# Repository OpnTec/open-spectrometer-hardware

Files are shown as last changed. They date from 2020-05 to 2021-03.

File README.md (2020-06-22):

# DIY Analytics Open Source Spectrometer




This repository provides hardware schematics and list of materials for the open spectrometer project to enable practitioners, students and citizen scientists to collect data with their spectrometer and have a good and fun learning experience. The open spectrometer project consists of a web cam, simple lasercut parts, battery casing and a suitable LED lightning component. The spectrometer connects to a computer via USB, where the user can run the scripts provided in this repository to run experiments and take measurements. Enjoy!

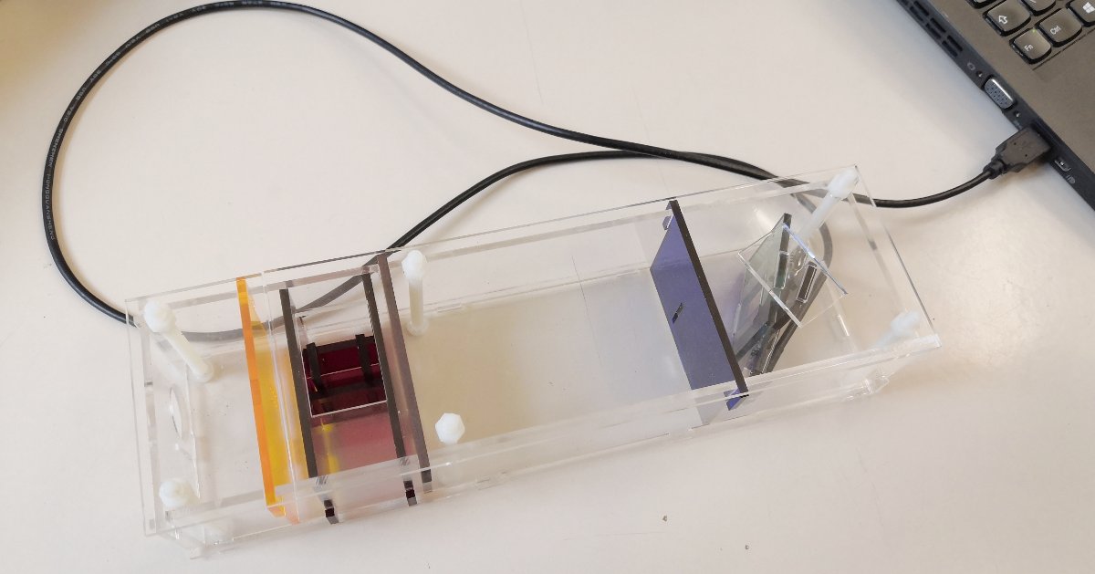
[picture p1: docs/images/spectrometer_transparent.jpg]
Open Source Spectrometer Open Source Spetrometer

A transparent version of the spectrometer for explanation purposes.

## Open Science and Goals

By definition science should be open and reproducible. So, the outcome of an experiment can be verified by anyone. Unfortunately today this is not always the case. In order to be able to verify experiments all components used should be openly accessible. This includes the software and hardware of scientific instruments. Our spectrometer project follows this path. By giving access to all layers of the device used in a scientific experiment users can develop a deep understanding how scientific measurements are taken and practitioners are able to critically understand the limitations of the particular instrument.

The spectrometer consists of a set of materials designed to be available and affordable anywhere in the world. The design's focus is to promote education about spectrometry and analytical chemistry, with the goal of empowering, stimulating and encouraging individuals to learn about their environment applying scientific methodologies. Furthermore, the goal of the tool is to enable practitioners to study open design, scientific programming, physics and to reflect about reproducibility in scientific practices.

## Communication

The spectrometer community is still small. There are overlaps with the Pocket Science Lab team. To stay connected with different community members we continue to use the PSLab Gitter channel for the beginning. We will set up a dedicated channel once the project is more established. Please join us here:
* [Pocket Science Channel](https://gitter.im/fossasia/pslab)

## Features and Implementation Status

- The bill of materials is available in the /components folder.
- The design files for the lasercut files are available in the /schematics folder.

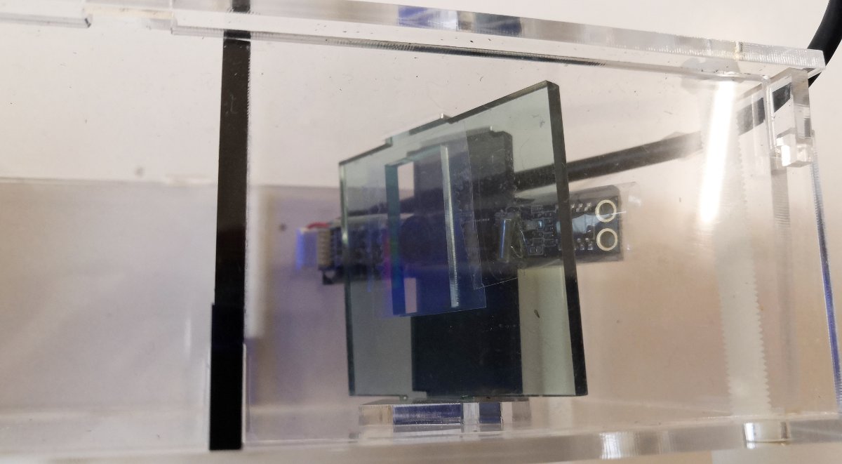
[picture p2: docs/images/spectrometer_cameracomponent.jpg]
Open Source Spectrometer Camera Component Open Source Spetrometer Camera Component

The camera component of the spectrometer in transparent casing.

Roadmap:

- improve the design of the wooden part holding the camera
- redesign the light side, in order to allow CFL light coming in without disassembling the whole spectrometer
- write a script that allows the user to control the spactrometer with a simple offline device
- reduce the size to fit in one 25x50cm board

## Software

To get the data from the spetrometer device practitioners can use the spectrometer Python scripts available in the project. 

## Contributors

Alessandro Volpato is the creator of the project. The work was done by merging concepts of the [Public Lab Spectrometer](https://publiclab.org/notes/abdul/10-13-2016/desktop-spectrometry-starter-kit-3-0-instructions), 
the [GaudiLabs spectrometer](http://www.gaudi.ch/GaudiLabs/?page_id=328) and creating new design features to simplify the assembly of a lasercut spetrometer.

## License

The repository is licenced under CERN Open Hardware Licence v1.2

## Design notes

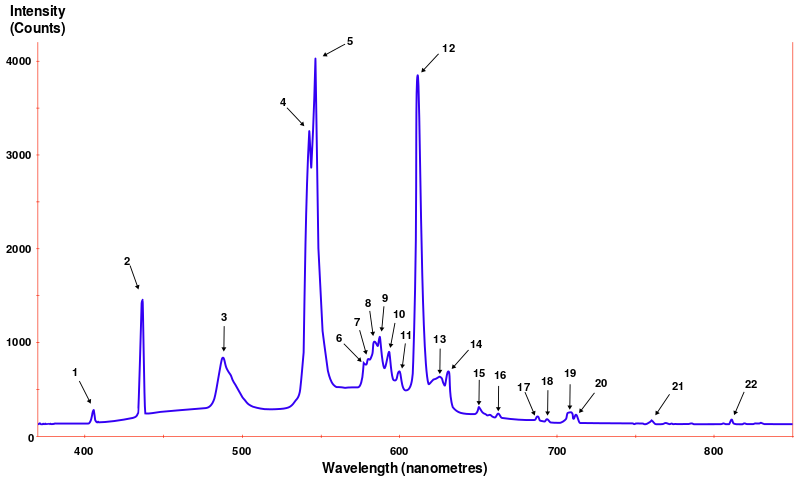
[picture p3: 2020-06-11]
open-spectrometer_v1/docs/images/Fluorescent_lighting_spectrum_peaks_labelled.svg.png

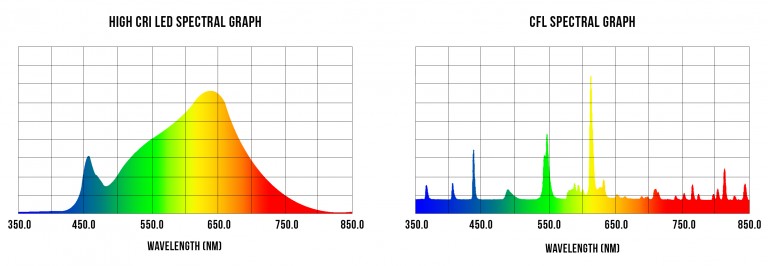
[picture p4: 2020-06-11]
open-spectrometer_v1/docs/images/High-CRI-vs-CFL-Spectrum-Graph-768x266.jpg

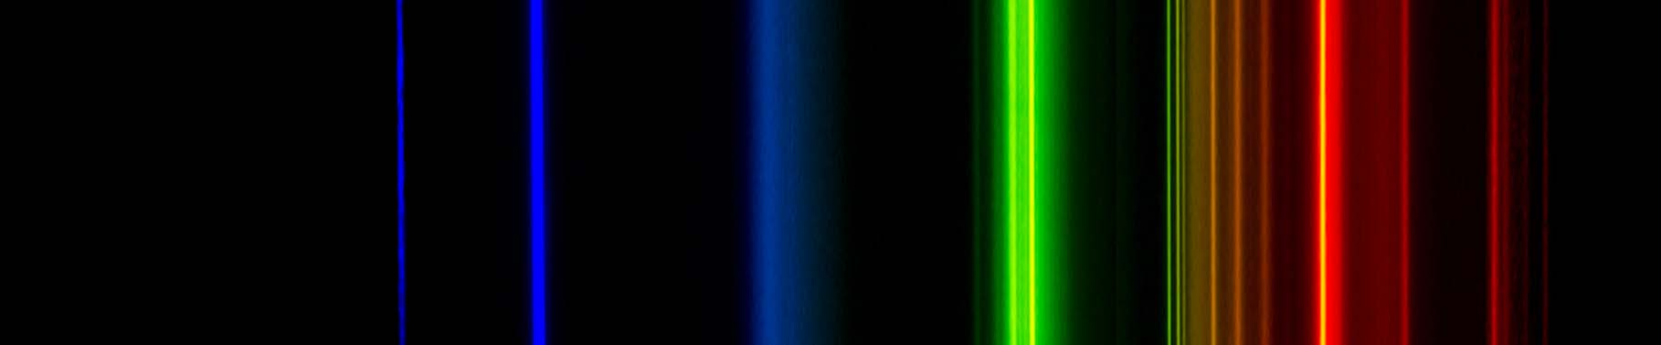
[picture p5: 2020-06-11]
open-spectrometer_v1/docs/images/3rdPolySnowy1818.jpg

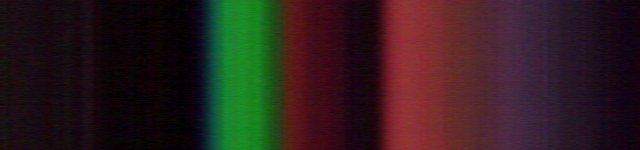
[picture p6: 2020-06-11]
open-spectrometer_v1/docs/images/2018_9_3_basil.png

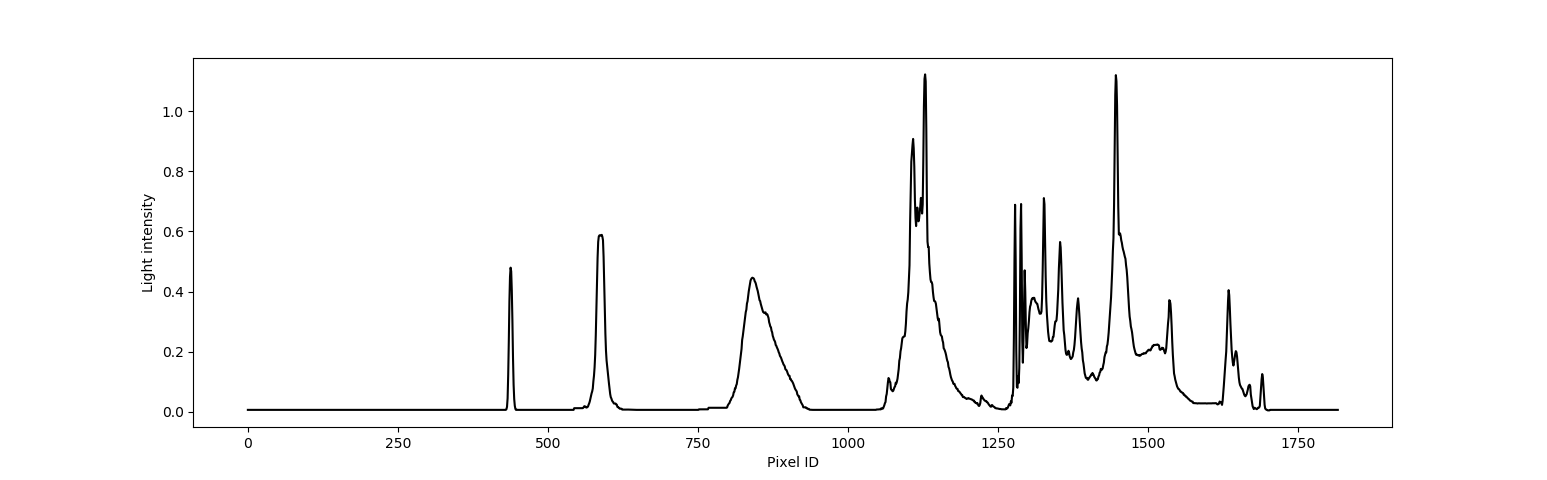
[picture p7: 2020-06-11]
open-spectrometer_v1/docs/images/cfl_BW.png

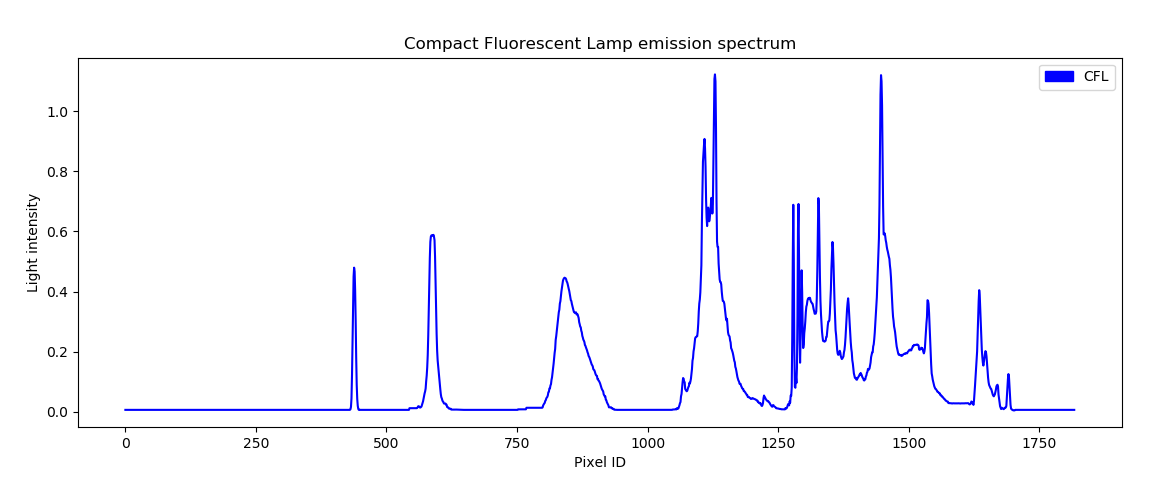
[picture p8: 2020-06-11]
open-spectrometer_v1/docs/images/CFL_rawPlot.png

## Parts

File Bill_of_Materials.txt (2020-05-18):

Bill of materials

- 2x MDF wood plates 25x50 cm (to be lasercut)
- Screws and nuts M5 60 mm
- Screws M15 and nuts M15 width max 3mm
- Anti slip tiny silicon pads
- Razor blades
- Duct tape / light tight tape
- Diffraction grating or "peeled" CD
- Webcam VIDEW JDEPC-05, lens 45°

- 1,5V batteries holder, double slot
- 2x 1,5V batteries
- White LED
- CFL (Compact Fluorescent Light) - for calibration (Notmandatory)
- Plug for the lightbulb

Suppliers:
MDF: Modulor, Berlin, Germany
https://www.modulor.de/en/

Screws and nuts M5x60
Aliexpress
Screws???
https://www.aliexpress.com/item/4000138361051.html

Screws and nuts M1.4x6
Aliexpress
https://www.aliexpress.com/item/32998910287.html
https://www.aliexpress.com/item/33002547187.html

Anti-slip pads
https://www.aliexpress.com/item/4000139088828.html

Slit / razor blades
https://www.edmundoptics.com/f/precision-air-slits/12136/
https://www.dm.de/muehle-rasierklingen-fuer-rasierhobel-p4028982008452.html

Duct tape
At bricolage market. It is used to cover the green LED on the camera module
To check if it's easier to turn off the LED directly

Diffraction grating / peeled cd
https://www.amazon.de/Rolle-Beugungsgitter-Folien-Linear-Linien/dp/B007G0MW2Q

Webcam VIDEW JDEPC-05, lens 45°, without IR filter
https://www.alibaba.com/product-detail/1-4-CMOS-Sensor-720P-camera_60667541444.html

AA battery x2
https://www.aliexpress.com/item/4000194009848.html

AA battery double case
https://www.aliexpress.com/item/32818907820.html

White LED
https://www.aliexpress.com/item/32505130071.html

CFL lightbulb (It's being phased out, xenon discharge lamps can substitute them)
https://www.amazon.de/Osram-Energiesparlampe-Stick-E27-363855/dp/B008OJWF9S/

CFL E27 lamp holder
https://www.amazon.de/kwmobile-Lampenfassung-Schalter-Lampenaufh%C3%A4ngung-Pendelleuchte/dp/B0769XRYXL

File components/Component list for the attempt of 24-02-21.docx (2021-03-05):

OLD Parts for assembling the driver circuit board

Suppliers:

Capacitors:

1x 0,1 µF

https://www.mouser.de/Passive-Components/Capacitors/Ceramic-Capacitors/MLCCs-Multilayer-Ceramic-Capacitors/Multilayer-Ceramic-Capacitors-MLCC-SMD-SMT/_/N-bkrdv?P=1z0wqusZ1yx4aw4Z1yzmou0&Keyword=capacitor&FS=True

1x 10 µF (tantalum) 10 µF (MLCC or tantalum 1206)
https://www.mouser.de/Passive-Components/Capacitors/Tantalum-Capacitors/Tantalum-Capacitors-Solid-SMD/_/N-75hr4?P=1z0wrkrZ1yzmotyZ1yzt832Z1yx4aw4

Resistors:

1x 2,2 kOhm (Better Reichelt)

https://www.conrad.de/de/o/smd-widerstaende-0241260.html?tfo_ATT_LOV_RESISTOR_DESIGN=0805&tfo_ATT_RESISTANCE_VALUE_NUM=2200%20%CE%A9

2x 150 Ohm (Better Reichelt)

https://www.conrad.de/de/o/smd-widerstaende-0241260.html?tfo_ATT_RESISTANCE_VALUE_NUM=150%20%CE%A9&tfo_ATT_LOV_RESISTOR_DESIGN=0805

1x 27 kOm (Better Reichelt)

https://www.mouser.de/Passive-Components/Resistors/_/N-5g9n?P=1yzmou0Z1yzekj3

1x 12 kOhm (Better Reichelt)

https://www.mouser.de/Passive-Components/Resistors/_/N-5g9n?P=1yzmou0Z1yzeki4

Transistor:

1x PNP

https://www.conrad.de/de/f/sot23-1724883.html?tfo_ATT_LOV_MODEL_TRANSISTORS=PNP

Hex-Inverter:

1x (Better Reichelt SMD HC 04 Inverter, Hex)

https://www.conrad.de/de/search.html?search=74HC04D&category=%1Ft12%1Fc1202469

Voltage regulator:

Reference:

https://tcd1304.wordpress.com/driving-circuit-and-pcb/

### Parts and components -> download all datasheets -> check 0603 dimensions

##### Drive circuit:

- C₃, C₄ 100 nF (MLCC 0805)
- C₂ 10 µF (MLCC or tantalum 1206) -> check dimension
- R₄, R₄ 150 Ω (0805)
- R₃ 2.2 kΩ (0805)
- U₂ 74HC04D (SOIC-14) Note: Hex inverter -> check direction
- T₁ 2SA1015 / 2SA1162 (SOT-23) Note: Transistor

##### LDO: low noise low drop-out voltage regulator

- U₁ LT1761-BYP (SOT-23-5) Note: High efficiency, step down, DC-DC converter Low Noise, Low Dropout Micropower Regulator
- R₂ 27 kΩ (0805)
- R₁ 12 kΩ (0805)
- C₁ 10 nF (MLCC 0805) -> check dimension
- C₅ 1 µF (MLCC 0805) -> check dimension

The LDO is an additional circuit to produce, low noise and smoother(?) power supply

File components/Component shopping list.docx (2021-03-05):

Current Version

Parts for assembling the driver circuit board

Supplier: Mouser

Make 1 shipment to check that the dimensions of the SMD parts match with the board!!!

Capacitors:

C1: https://www.mouser.de/ProductDetail/KEMET/C0805C103K8RACTU/?qs=cw4evkOYbeKGik5IKerAPQ%3D%3D

C2: https://www.mouser.de/ProductDetail/ROHM-Semiconductor/TCA0J106M8R/?qs=sGAEpiMZZMsh%252B1woXyUXj69kqxOlrVKzuvW12Vm0Wbs%3D

C3,C4: https://www.mouser.de/ProductDetail/KEMET/C0805C104K9RACAUTO/?qs=ds50AKTGxA84SWre%252BvImOA%3D%3D

C5: https://www.mouser.de/ProductDetail/KEMET/C0805C105K9RACTU/?qs=Nnkldhwoc36daYb4WU%2Fecw%3D%3D

Resistors:

R1: https://www.mouser.de/ProductDetail/Panasonic/ERJ-U06J123V/?qs=sGAEpiMZZMtlubZbdhIBIAOOKAsNLlB%252BU0Q0TtVw5QE%3D

R2: https://www.mouser.de/ProductDetail/Panasonic/ERJ-T06J273V/?qs=sGAEpiMZZMtlubZbdhIBIK7FbVYKWV6W038uxDWOpRk%3D

R3: https://www.mouser.de/ProductDetail/Panasonic/ERJ-U06J222V/?qs=Yyy8avaXlIt9u%2Fm70g0idQ%3D%3D

R4,R5: https://www.mouser.de/ProductDetail/Panasonic/ERJ-U06J151V/?qs=Yyy8avaXlIvde5Eu83MNpg%3D%3D

Transistor:

T1: https://www.mouser.de/ProductDetail/Toshiba/2SA1162-GRLF/?qs=iCzJi%2FIZBF4pKAB14b5rPg%3D%3D

Units:

U1: https://www.mouser.de/ProductDetail/Analog-Devices/LT1761ES5-BYPTRPBF/?qs=ytflclh7QUVO1tv%2FV6bsow%3D%3D

U2: https://www.mouser.de/ProductDetail/Nexperia/74HC04D-Q100118/?qs=%2Fha2pyFadugYAPSa%2Fr415QHV4LwjhLocoaB0htU8Y3E%3D

Reference:

https://tcd1304.wordpress.com/driving-circuit-and-pcb/

### Parts and components -> download all datasheets -> check 0603 dimensions

##### Drive circuit:

- C₃, C₄ 100 nF (MLCC 0805)
- C₂ 10 µF (MLCC or tantalum 1206) -> check dimension
- R₄, R5 150 Ω (0805)
- R₃ 2.2 kΩ (0805)
- U₂ 74HC04D (SOIC-14) Note: Hex inverter -> check direction
- T₁ 2SA1015 / 2SA1162 (SOT-23) Note: Transistor

##### LDO: low noise low drop-out voltage regulator

- U₁ LT1761-BYP (SOT-23-5) Note: High efficiency, step down, DC-DC converter Low Noise, Low Dropout Micropower Regulator
- R₂ 27 kΩ (0805)
- R₁ 12 kΩ (0805)
- C₁ 10 nF (MLCC 0805) -> check dimension
- C₅ 1 µF (MLCC 0805) -> check dimension

The LDO is an additional circuit to produce, low noise and smoother(?) power supply

Connecting to NUCLEO

Inner side

1 A3

2 A1

3 A0

4 +5V

5 GND

6 A5

outer side

OLD Parts for assembling the driver circuit board

Suppliers:

Capacitors:

1x 0,1 µF

https://www.mouser.de/Passive-Components/Capacitors/Ceramic-Capacitors/MLCCs-Multilayer-Ceramic-Capacitors/Multilayer-Ceramic-Capacitors-MLCC-SMD-SMT/_/N-bkrdv?P=1z0wqusZ1yx4aw4Z1yzmou0&Keyword=capacitor&FS=True

1x 10 µF (tantalum) 10 µF (MLCC or tantalum 1206)
https://www.mouser.de/Passive-Components/Capacitors/Tantalum-Capacitors/Tantalum-Capacitors-Solid-SMD/_/N-75hr4?P=1z0wrkrZ1yzmotyZ1yzt832Z1yx4aw4

Resistors:

1x 2,2 kOhm (Better Reichelt)

https://www.conrad.de/de/o/smd-widerstaende-0241260.html?tfo_ATT_LOV_RESISTOR_DESIGN=0805&tfo_ATT_RESISTANCE_VALUE_NUM=2200%20%CE%A9

2x 150 Ohm (Better Reichelt)

https://www.conrad.de/de/o/smd-widerstaende-0241260.html?tfo_ATT_RESISTANCE_VALUE_NUM=150%20%CE%A9&tfo_ATT_LOV_RESISTOR_DESIGN=0805

1x 27 kOm (Better Reichelt)

https://www.mouser.de/Passive-Components/Resistors/_/N-5g9n?P=1yzmou0Z1yzekj3

1x 12 kOhm (Better Reichelt)

https://www.mouser.de/Passive-Components/Resistors/_/N-5g9n?P=1yzmou0Z1yzeki4

Transistor:

1x PNP

https://www.conrad.de/de/f/sot23-1724883.html?tfo_ATT_LOV_MODEL_TRANSISTORS=PNP

Hex-Inverter:

1x (Better Reichelt SMD HC 04 Inverter, Hex)

https://www.conrad.de/de/search.html?search=74HC04D&category=%1Ft12%1Fc1202469

Voltage regulator:

Reference:

https://tcd1304.wordpress.com/driving-circuit-and-pcb/

### Parts and components -> download all datasheets -> check 0603 dimensions

##### Drive circuit:

- C₃, C₄ 100 nF (MLCC 0805)
- C₂ 10 µF (MLCC or tantalum 1206) -> check dimension
- R₄, R₄ 150 Ω (0805)
- R₃ 2.2 kΩ (0805)
- U₂ 74HC04D (SOIC-14) Note: Hex inverter -> check direction
- T₁ 2SA1015 / 2SA1162 (SOT-23) Note: Transistor

##### LDO: low noise low drop-out voltage regulator

- U₁ LT1761-BYP (SOT-23-5) Note: High efficiency, step down, DC-DC converter Low Noise, Low Dropout Micropower Regulator
- R₂ 27 kΩ (0805)
- R₁ 12 kΩ (0805)
- C₁ 10 nF (MLCC 0805) -> check dimension
- C₅ 1 µF (MLCC 0805) -> check dimension

The LDO is an additional circuit to produce, low noise and smoother(?) power supply

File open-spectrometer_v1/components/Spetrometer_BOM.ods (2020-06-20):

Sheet: PSLab_BoM
# | Description | Manufacturer | Mfr. Part Number | Part | References | Value | Footprint | Quantity Per Device | Datasheet | Digikey | Mouser | RS | Farnell
1 | MDF wood plates 25x50 cm (to be lasercut) |  |  |  |  |  |  | 2
2 | Screws and nuts M5 60 mm |  |  |  |  |  |  | 6
3 | Screws M15 and nuts M15 width max 3mm |  |  |  |  |  |  | 6
4 | Anti slip tiny silicon pads
5 | Razor blades
6 | Duct tape / light tight tape
7 | Diffraction grating or "peeled" CD
8 | Webcam VIDEW JDEPC-05, lens 45°
9 | 1,5V batteries holder, double slot
10 | 2x 1,5V batteries
11 | White LED
12 | CFL (Compact Fluorescent Light) - for calibration (Notmandatory)
13 | Plug for the lightbulb

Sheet: Suppliers
Suppliers:
MDF: Modulor, Berlin, Germany
https://www.modulor.de/en/
Screws and nuts M5x60
Aliexpress
Screws???
https://www.aliexpress.com/item/4000138361051.html
Screws and nuts M1.4x6
Aliexpress
https://www.aliexpress.com/item/32998910287.html
https://www.aliexpress.com/item/33002547187.html
Anti-slip pads
https://www.aliexpress.com/item/4000139088828.html
Slit / razor blades
https://www.edmundoptics.com/f/precision-air-slits/12136/
https://www.dm.de/muehle-rasierklingen-fuer-rasierhobel-p4028982008452.html
Duct tape
At bricolage market. It is used to cover the green LED on the camera module
To check if it's easier to turn off the LED directly
Diffraction grating / peeled cd
https://www.amazon.de/Rolle-Beugungsgitter-Folien-Linear-Linien/dp/B007G0MW2Q
Webcam VIDEW JDEPC-05, lens 45°, without IR filter
https://www.alibaba.com/product-detail/1-4-CMOS-Sensor-720P-camera_60667541444.html
AA battery x2
https://www.aliexpress.com/item/4000194009848.html
AA battery double case
https://www.aliexpress.com/item/32818907820.html
White LED
https://www.aliexpress.com/item/32505130071.html
CFL lightbulb (It's being phased out, xenon discharge lamps can substitute them)
https://www.amazon.de/Osram-Energiesparlampe-Stick-E27-363855/dp/B008OJWF9S/
CFL E27 lamp holder
https://www.amazon.de/kwmobile-Lampenfassung-Schalter-Lampenaufh%C3%A4ngung-Pendelleuchte/dp/B0769XRYXL

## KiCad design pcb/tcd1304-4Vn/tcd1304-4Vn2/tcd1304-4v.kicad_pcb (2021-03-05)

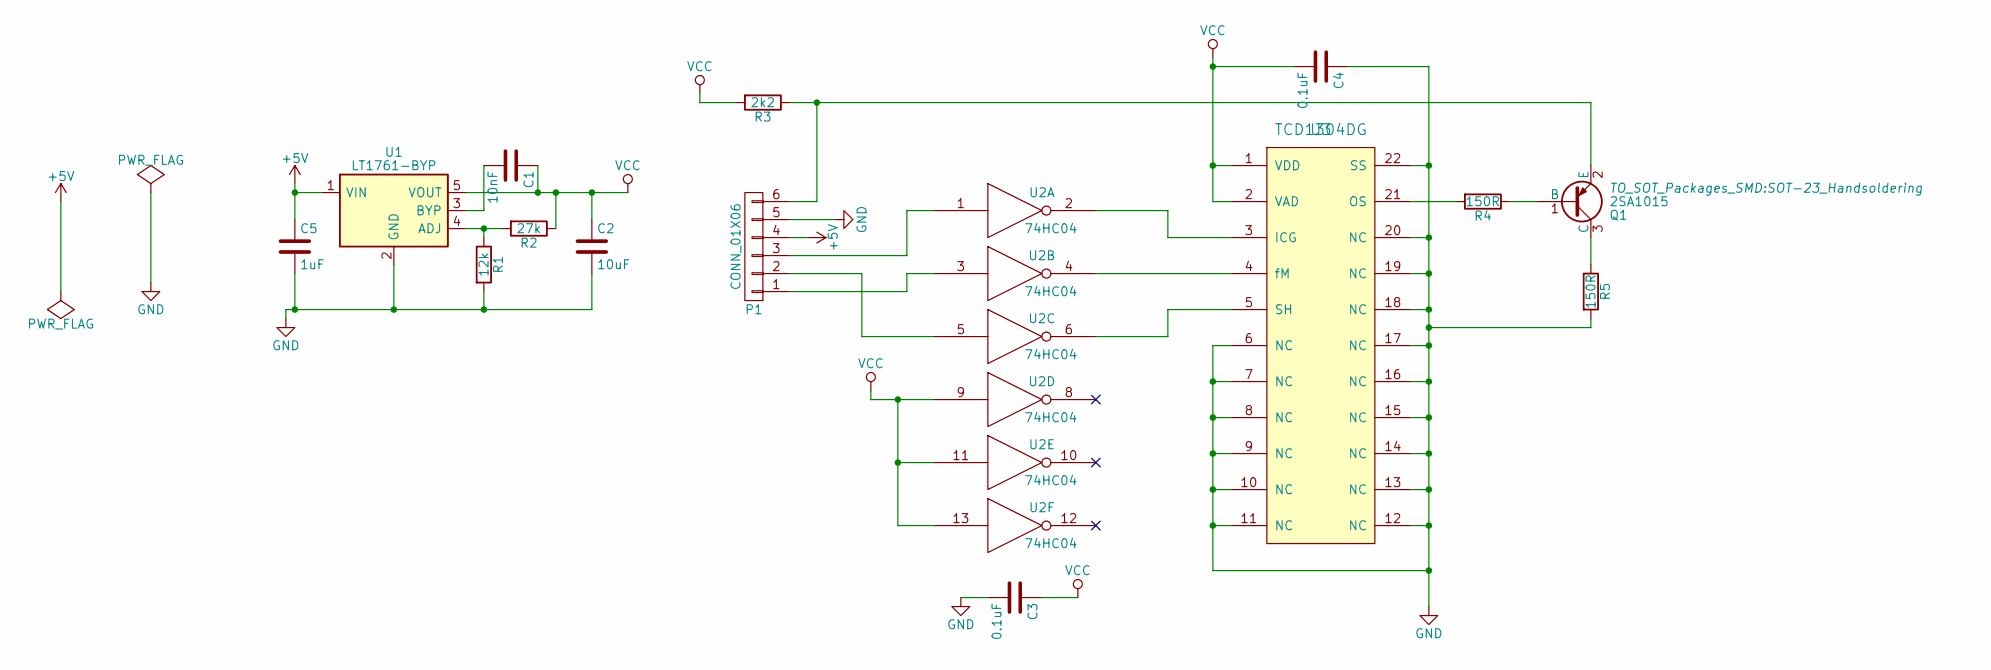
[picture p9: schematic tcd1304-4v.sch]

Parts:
C1: 10nF; C_0805
C2: 10uF; C_1206
C3, C4: 0.1uF; C_0805
C5: 1uF; C_0805
P1: CONN_01X06; Pin_Header_Straight_1x06
Q1: 2SA1015; SOT-23_Handsoldering
R1: 12k; C_0805
R2: 27k; C_0805
R3: 2k2; C_0805
R4, R5: 150R; C_0805
U1: LT1761-BYP; SOT-23-5-handsoldering
U2: 74HC04; SOIC-14_3.9x8.7mm_Pitch1.27mm
U3: TCD1304DG; DIP-22_W10.16mm

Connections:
+5V: C5.1, P1.4, U1.1 (VIN)
GND: C2.2, C3.2, C4.1, C5.2, P1.5, R1.2, R5.2, U1.2 (GND), U2.7 (GND), U3.6 (NC), U3.7 (NC), U3.8 (NC), U3.9 (NC), U3.10 (NC), U3.11 (NC), U3.12 (NC), U3.13 (NC), U3.14 (NC), U3.15 (NC), U3.16 (NC), U3.17 (NC), U3.18 (NC), U3.19 (NC), U3.20 (NC), U3.22 (SS)
unnamed: C1.2, U1.3 (BYP)
unnamed: P1.1, U2.3
unnamed: P1.2, U2.5
unnamed: P1.3, U2.1
unnamed: P1.6, Q1.2 (E), R3.1
unnamed: Q1.1 (B), R4.1
unnamed: Q1.3 (C), R5.1
unnamed: R1.1, R2.2, U1.4 (ADJ)
unnamed: R4.2, U3.21 (OS)
unnamed: U2.2, U3.3 (ICG)
unnamed: U2.4, U3.4 (fM)
unnamed: U2.6, U3.5 (SH)
VCC: C1.1, C2.1, C3.1, C4.2, R2.1, R3.2, U1.5 (VOUT), U2.9, U2.11, U2.13, U2.14 (VCC), U3.1 (VDD), U3.2 (VAD)

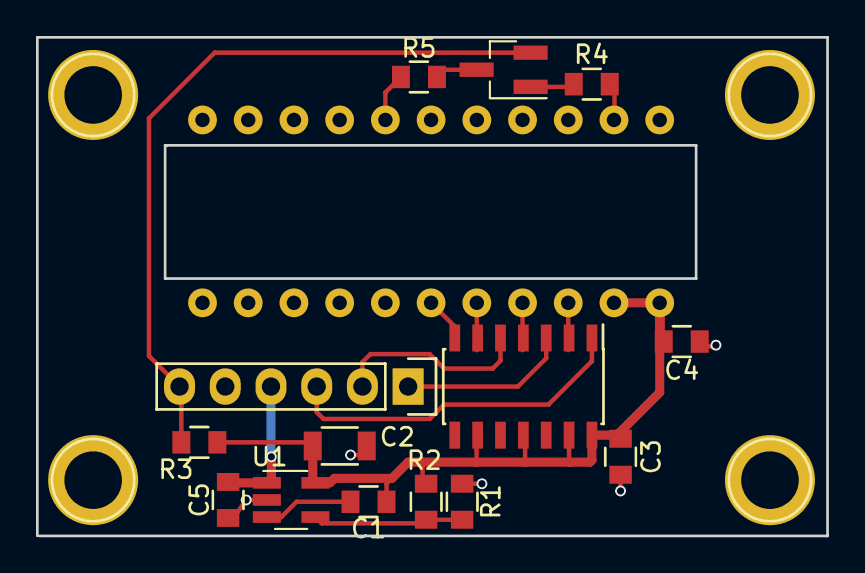
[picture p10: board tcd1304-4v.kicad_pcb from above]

Board: 2 copper layers, 43.9 x 27.7 mm, 15 parts (1 on the bottom side), 15 nets.

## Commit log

2020-06-12 updated docs, and reorganized repo
    [Spetrometer_BOM.ods]
2021-03-05 spectrometer v2
    [Spetrometer_BOM.ods, tcd1304-4v-B.Cu.gbl, tcd1304-4v-B.Cu.gbr, tcd1304-4v-B.Mask.gbr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]
